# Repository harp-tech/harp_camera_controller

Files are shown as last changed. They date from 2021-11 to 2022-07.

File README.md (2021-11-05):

# Harp Camera Controlelr

This device contains the necessary circuitry to synchronously control and supply 2 cameras.

# Licensing

The code, designs, documentation, and photos available in this repository is free: you can redistribute it and/or modify it under the terms of the used license.
Each subdirectory will contain a license or, possibly, a set of licenses if it involves both hardware and software. Check files named LICENSE.

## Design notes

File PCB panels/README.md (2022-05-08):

# Harp Camera Controller Panels

## Licensing

The designs, documentation, and photos available in this repository are free: you can redistribute it and/or modify it under the terms of the used license.
Check file named LICENSE.

Copyright Filipe Carvalho 2021-2022

<br />This work is licensed under a <a rel="license" href="http://creativecommons.org/licenses/by-nc-sa/3.0/igo/">Creative Commons Attribution-NonCommercial-ShareAlike 3.0 IGO License</a>.

If your are interested in obtaining a license to sell this device, please contact info@oeps.tech

[1]: https://docs.google.com/spreadsheets/d/1aobmmEzBDethzIlrm1eg0eYkBqlyX3s9WbA9KgRwVQI/edit?usp=sharing

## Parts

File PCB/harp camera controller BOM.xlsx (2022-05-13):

Qty | Value | Package | Parts | MPN | Type
PCB COMPONENTS
2 | SN74LVC1G125DBVT | SOT23-5 | IC7, IC8 | SN74LVC1G125DBVT | SMD | -
1 | 74HCT125SO14 | SO14 | U5 | 74HCT125D,653 | SMD | -
3 | 74LVC126ASO14 | SO14 | U2, U3, U4 | 74LVC126AD,118 | SMD | -
2 | 74LVC1G240DBV | SOT23-5 | IC2, IC3 | SN74LVC1G240DBVR | SMD | -
1 | ATXMEGA32A4U-AU | QFP80P1200X1200X120-44N | IC6 | ATXMEGA32A4U-AUR | SMD | -
4 | BC850 | SOT23 | T1, T2, T3, T4 | BC850C,215 | SMD | -
1 | 330 Ohms @ 100MHz | R0603 | F1 | BLM18SG331TN1D | SMD | -
3 | BNC plug | 0731000105 | X3, X4, X5 | 73100-0105 | TH | -
23 | 100nF | C0402 | C2, C4, C5, C6, C8, C9, C14, C15, C16, C18, C19, C20, C24, C25, C26, C27, C28, C29, C31, C33, C34, C36, C38 | C1005X7R1H104K050BB | SMD | -
3 | 330pF | C0402 | C22, C30, C37 | C0402C331J5GACTU | SMD | -
1 | 4.7nF | C0402 | C1 | 885012205084 | SMD | -
2 | 47pF | C0402 | C10, C13 | 04025A470JAT2A | SMD | -
1 | 180nF | C0603 | C11 | GCG188R91H184KA01D | SMD
5 | 4.7uF | C0603 | C12, C21, C23, C32, C35 | C1608X6S1C475K080AC | SMD | -
1 | 4.7uF | C0805 | C3 | CL21A475KLCLQNC | SMD
1 | 100uF 16V | CT7343 | C17 | T491D107K016AT7280 | SMD
1 | 100u 25V | TT2D6 | C7 | EEU-FM1E101B | SMD | -
1 | DC_JACK2.1MM | DC_POWER_INPUT_2.1MM | PWR1 | 163-179PH-EX | TH | -
1 | FT232RL | SSOP28 | IC4 | FT232RL-REEL | SMD | -
1 | 10uH 3A | L_IHLP_PADS | L1 | IHLP2525CZER100M01 | SMD
2 | RED_LEDs | 569-011X-X00_LED_ARRAY | LED1, LED2 | 5690-111-100F | TH | -
1 | LT1765 | TSSOP16EXP | U1 | LT1765EFE#PBF | SMD | -
1 | PROG HEADER | MA03-2 | SV1 | 61300621121 | TH | -
1 | OSCILLATOR | OSCILLATOR_3.2X2.5 | OSC1 | O 32,0-JT32C-A-K-3,3-LF | SMD | ALTERNATIVE: DSC1001CI5-032.0000
1 | 10R | R0402 | R35 | CRCW040210R0FKEDC | SMD | -
18 | 10k | R0402 | R2, R3, R4, R5, R6, R7, R8, R10, R11, R15, R17, R21, R22, R23, R32, R33, R34, R36 | CRCW040210K0FKED | SMD | -
1 | 10k 0.1% | R0402 | R13 | CPF0402B10KE1 | SMD | -
6 | 1k | R0402 | R14, R16, R24, R25, R28, R29 | CRCW04021K00FKEDC | SMD | -
1 | 34k 0.1% | R0402 | R12 | ERA2AEB3402X | SMD
4 | 330R | R0402 | R26, R27, R30, R31 | RC0402FR-07330RL | SMD | -
4 | 100R | R0603 | R1, R18, R19, R20 | ERJ-3EKF1000V | SMD | -
1 | 40R@100MHz | R0805 | R9 | MI0805K400R-10 | SMD | -
2 | RJ45 | RJ45-NO-SHIELD | X1, X2 | 215877-1 | TH | -
1 | SSB43L-E3 | SMB | D1 | SSB43L-E3/52T | SMD | -
1 | CMDSH-3 | SOD323-R | D2 | CMDSH-3 | SMD | -
1 | SI8610BC-B-IS | SO-08 | IC10 | SI8610EC-B-IS | SMD | ALTERNATIVE: ADUM110N0BRZ
2 | CLCK_JACK | 35RASMT2BHNTRX | CLOCK_IN, CLOCK_OUT | 35RASMT2BHNTRX | SMD | -
2 | TLV70033DDCR | TSOT23-5 | IC5, IC9 | TLV70033DDCR | SMD | SIMILAR & AVAILABLE = LP5951MFX-3.3/NOPB >> DIGIKEY_PN: 296-47807-2-ND MOUSER_PN: 926-LP5951MFX33NOPB
1 | mini USB | 240-0002-1 | USB1 | UX60-MB-5S8 | SMD | END OF LIFE COMPONENT BY SEPTEMBER 2021
1 | USBLC6-2SC6 | SOT23-6L | IC1 | USBLC6-2SC6 | SMD | EQUIVALENT: RCLAMP0504S.TCT
POST-PRODUCTION
1 |  |  | Front Panel PCB | PCBWAY
1 |  |  | Rear Panel PCB | PCBWAY
1 |  |  | Enclosure | B5-080BK
4 |  |  | Bumper Cylindrical Dome 9.53mm | SJ-5306-CLEAR-3000/CASE
ACCESSORIES
1 |  |  | 3.5mm stereo jack cable 1.2 m, Black | AV13646
1 |  |  | 0.9 left angle USB cable | USB2HABM3RA
NOTES
 |  |  |  | Number of unique parts | 39
 |  |  |  | Number of unique SMD parts | 34
 |  |  |  | Number of unique TH parts | 5
 |  |  |  | Number of SMD parts | 101
 |  |  |  | Number of TH parts | 9
 |  | Optional
 |  | Holder: MF80BK2

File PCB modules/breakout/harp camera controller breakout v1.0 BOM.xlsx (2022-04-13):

Qty | Value | Package | Parts | MPN | Type | Distributor | Distributor PN
ASSEMBLY HOUSE
1 | Ultra-Low-Noise LDO 3.3V 250mA | SOT-23-5 | X1 | 215877-1 | TH | Farnell | 3363144
1 | Terminal block 7 ways 2.54 mm |  | X2 | 282834-7 | TH | Farnell | 3792975
POST-PRODUCTION
1 | Small Ethernet cable
NOTES
 |  |  |  | Number of unique parts | 2
 |  |  |  | Number of SMD parts | 0
 |  |  |  | Number of TH parts | 2

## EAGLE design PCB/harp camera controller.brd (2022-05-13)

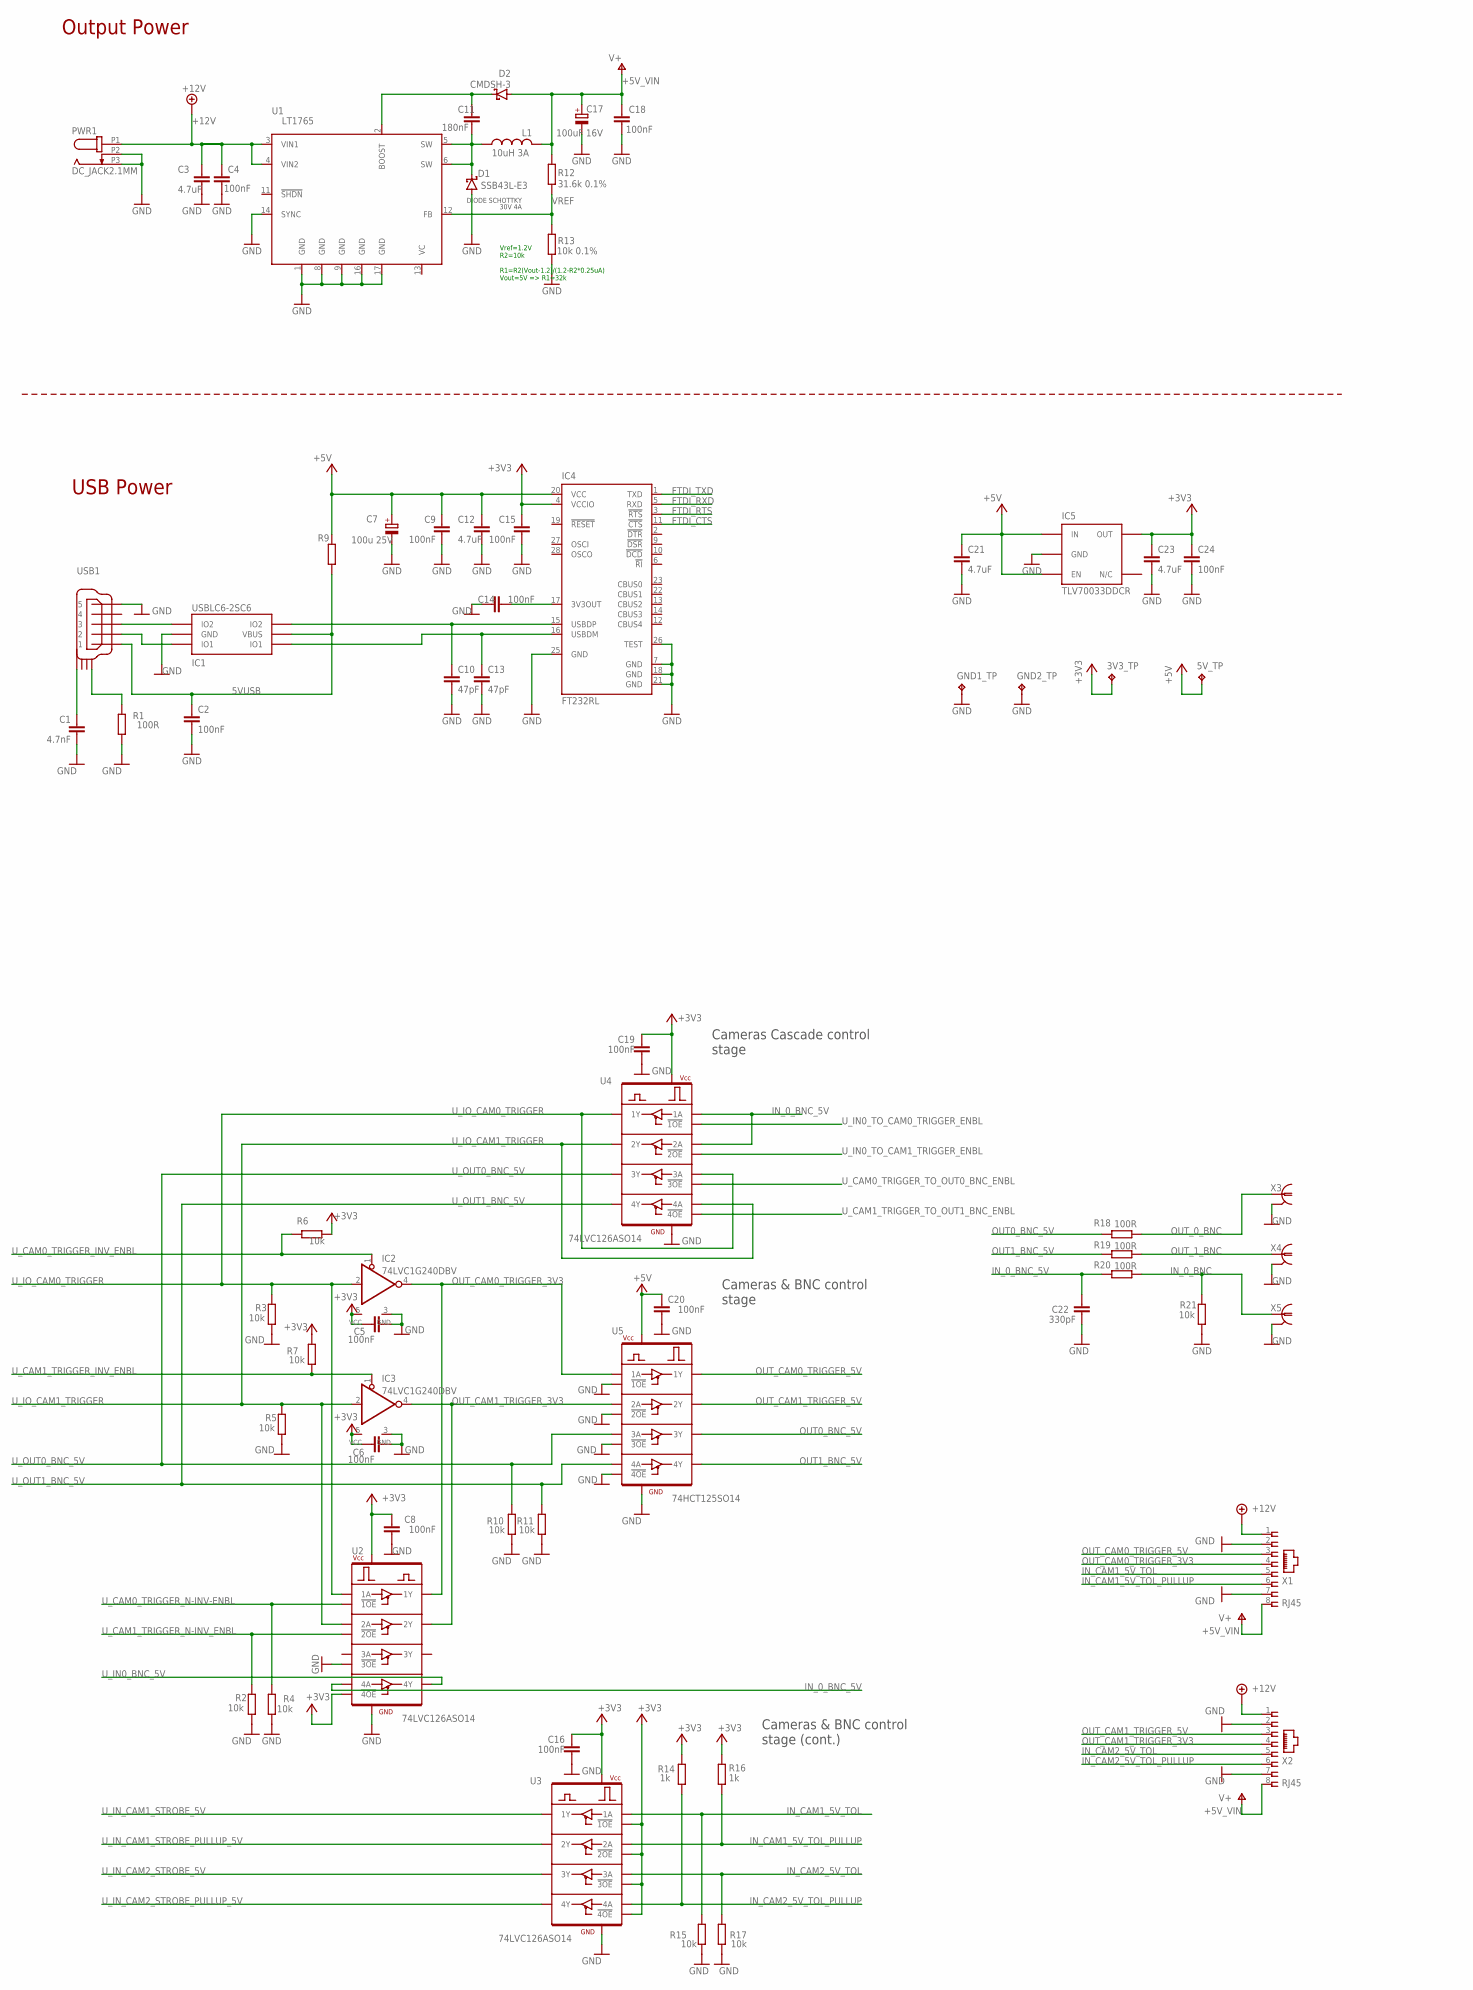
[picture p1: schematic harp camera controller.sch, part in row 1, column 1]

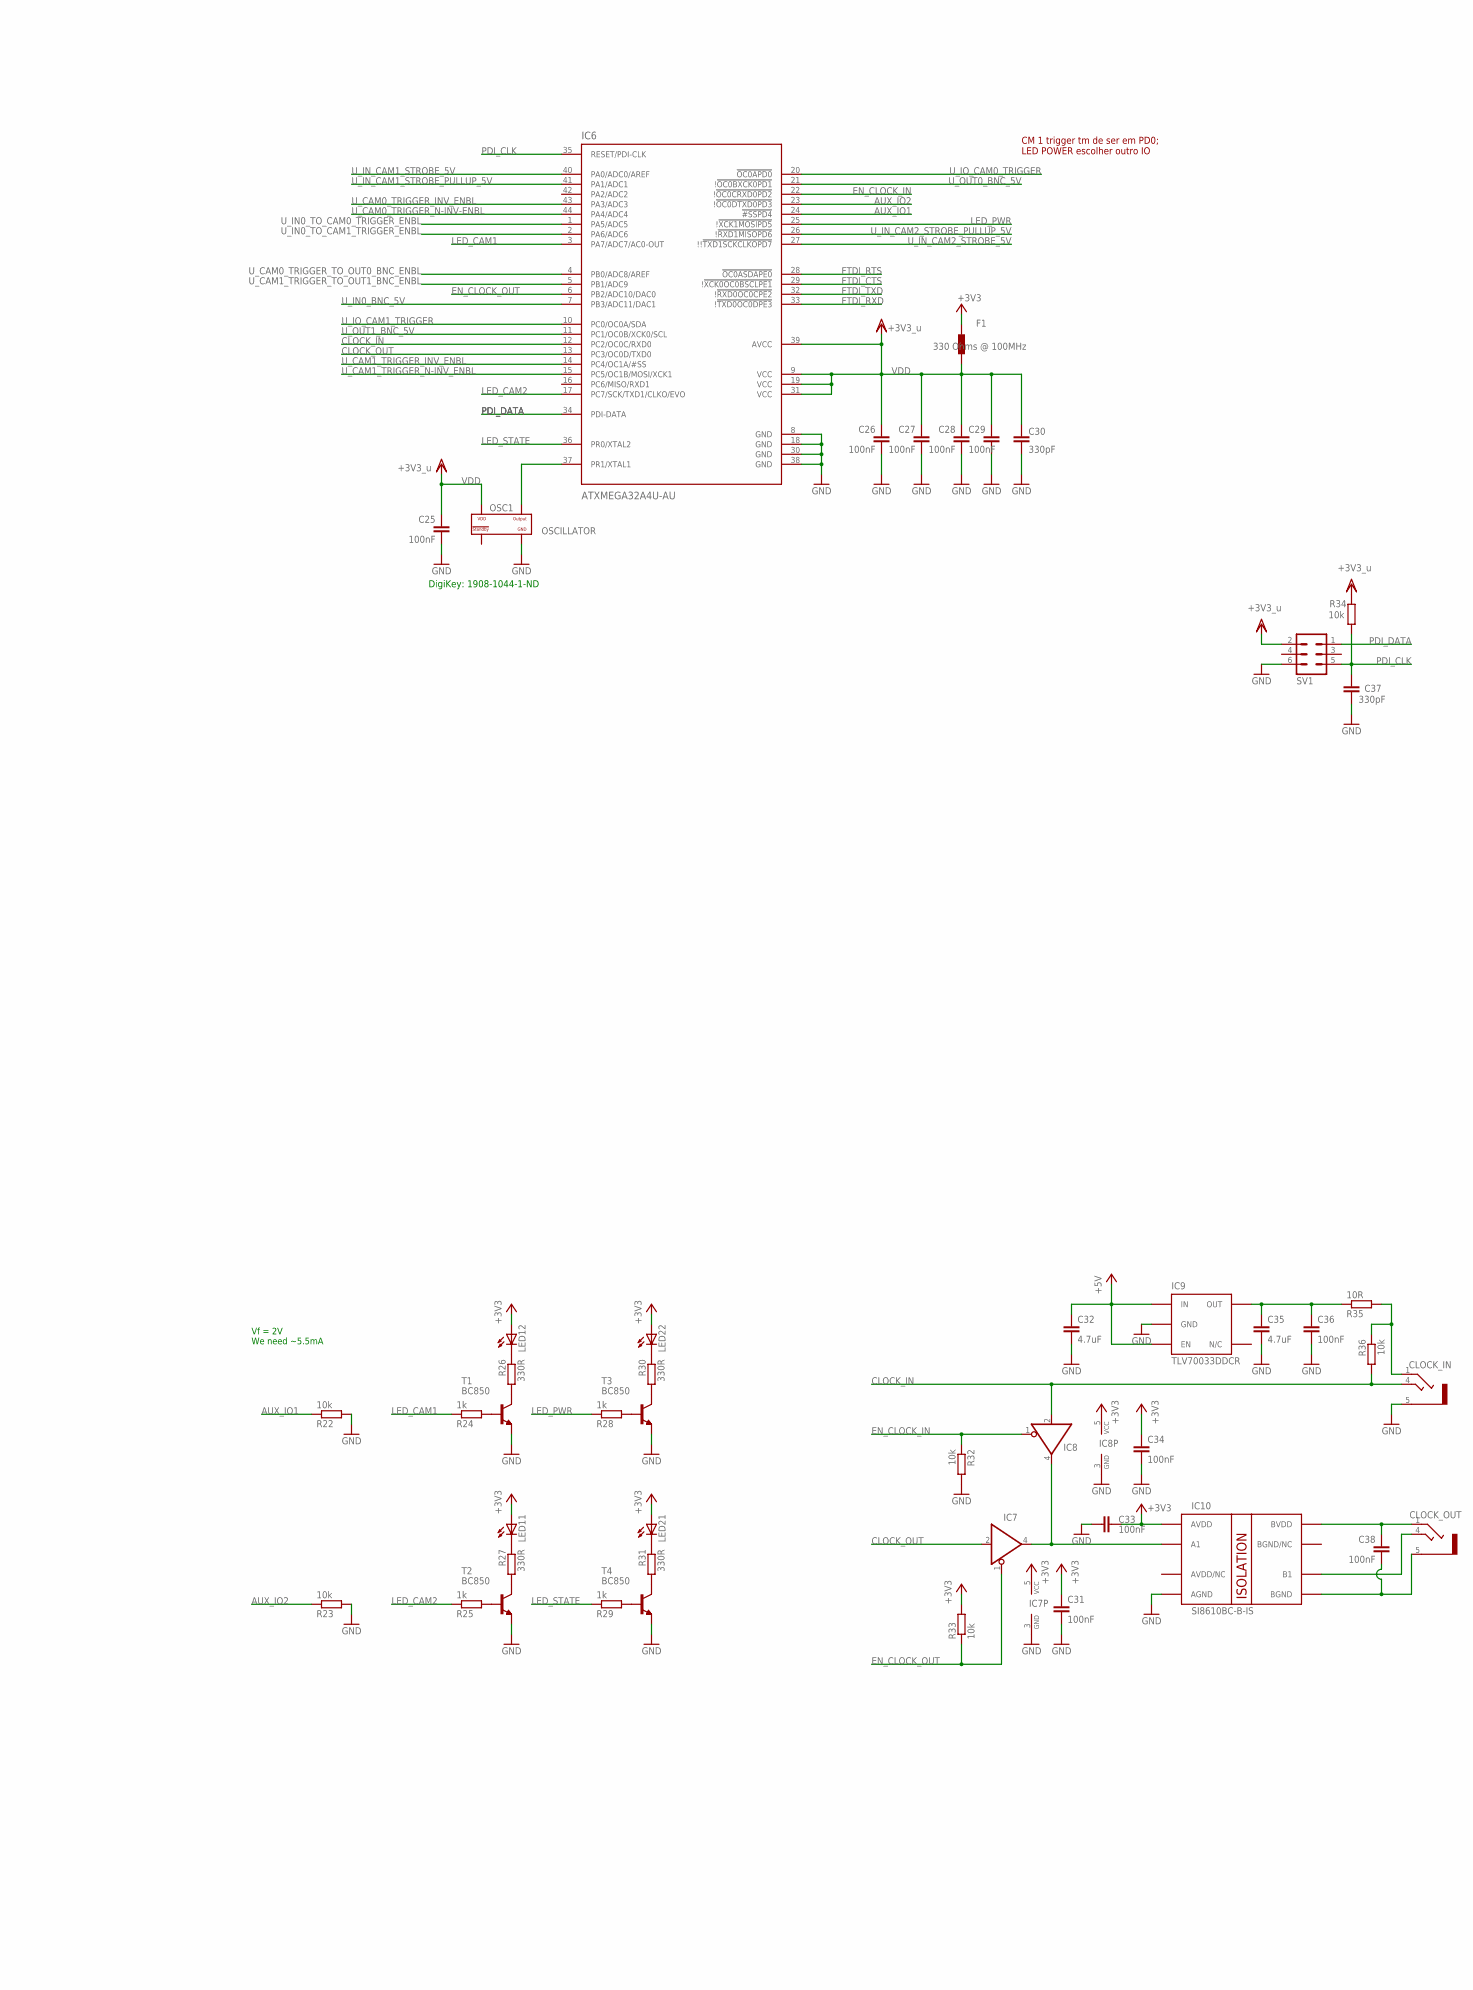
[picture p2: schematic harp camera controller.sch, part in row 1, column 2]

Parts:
3V3_TP, 5V_TP: TPPAD1-13; P1-13; MOUSER_PN N.A.; DIGIKEY_PN N.A.
C1: 4.7nF; C0402; MPN 885012205084; DIGIKEY_PN 732-12234-1-ND
C2, C4, C5, C6, C8, C9, C14, C15, C16, C18, C19, C20, C24, C25, C26, C27, C28, C29, C31, C33, C34, C36, C38: 100nF; C0402; MPN C1005X7R1H104K050BB; DIGIKEY_PN 445-5932-1-ND
C3: 4.7uF; C0805; MPN CL21A475KLCLQNC; DIGIKEY_PN 1276-6722-1-ND
C7: 100u 25V; TT2D6; MPN EEU-FM1E101B; DIGIKEY_PN P19702CT-ND
C10, C13: 47pF; C0402; MPN 04025A470JAT2A; DIGIKEY_PN 478-1078-1-ND
C11: 180nF; C0603; MPN GCG188R91H184KA01D; DIGIKEY_PN 490-GCG188R91H184KA01DCT-ND
C12, C21, C23, C32, C35: 4.7uF; C0603; MPN C1608X6S1C475K080AC; DIGIKEY_PN 445-9118-1-ND
C17: 100uF 16V; CT7343; MPN T491D107K016AT7280; DIGIKEY_PN 399-18066-1-ND
C22, C30, C37: 330pF; C0402; MPN C0402C331J5GACTU; DIGIKEY_PN 399-7787-1-ND
CLOCK_IN: CLCK_JACK; 35RASMT2BHNTRX; MOUSER_PN 502-35RASMT2BHNTRX; DIGIKEY_PN SC1489-1-ND
CLOCK_OUT: CLCK_JACK; 35RASMT2BHNTRX; MOUSER_PN 502-35RASMT2BHNTRX; DIGIKEY_PN SC1489-1-ND
D1: SSB43L-E3; SMB; MOUSER_PN 625-SSB43L-E3; DIGIKEY_PN SSB43L-E3/52TGICT-ND
D2: CMDSH-3; SOD323-R; MOUSER_PN 610-CMDSH-3; DIGIKEY_PN 1514-CMDSH-3TRPBFREECT-ND
F1: 330 Ohms @ 100MHz; R0603; MOUSER_PN 81-BLM18SG331TN1D; DIGIKEY_PN 490-3997-1-ND
GND1_TP, GND2_TP: TPPAD1-13; P1-13; MOUSER_PN N.A.; DIGIKEY_PN N.A.
IC1: USBLC6-2SC6; SOT23-6L; MOUSER_PN 511-USBLC6-2SC6; DIGIKEY_PN 497-5235-1-ND
IC2, IC3: 74LVC1G240DBV; SOT23-5; MOUSER_PN 595-SN74LVC1G240DBVR; DIGIKEY_PN 296-11609-1-ND
IC4: FT232RL; SSOP28; MOUSER_PN 895-FT232RL; DIGIKEY_PN 768-1007-1-ND
IC5, IC9: TLV70033DDCR; TSOT23-5; MOUSER_PN 595-TLV70033DDCR; DIGIKEY_PN 296-27937-1-ND
IC6: ATXMEGA32A4U-AU; QFP80P1200X1200X120-44N; MOUSER_PN 556-ATXMEGA32A4U-AU; DIGIKEY_PN ATXMEGA32A4U-AURCT-ND
IC7, IC8: SN74LVC1G125DBVT; SOT23-5; MOUSER_PN 595-SN74LVC1G125DBVT; DIGIKEY_PN 296-26595-1-ND
IC10: SI8610BC-B-IS; SO-08; MOUSER_PN 634-SI8610EC-B-IS; DIGIKEY_PN 336-2058-5-ND
L1: 10uH 3A; L_IHLP_PADS; MOUSER_PN 70-IHLP2525CZER100M0; DIGIKEY_PN 541-1013-2-ND
LED1, LED2: RED_LEDs; 569-011X-X00_LED_ARRAY; MOUSER_PN 645-569-0111-100F; DIGIKEY_PN 350-1782-ND
OSC1: OSCILLATOR; OSCILLATOR_3.2X2.5; MOUSER_PN N.A. - ALTERNATIVE ONLY; DIGIKEY_PN 1908-1044-1-ND
PWR1: DC_JACK2.1MM; DC_POWER_INPUT_2.1MM; MOUSER_PN 163-179PH; DIGIKEY_PN DIGIKEY N.A.
R1, R18, R19, R20: 100R; R0603; MPN ERJ-3EKF1000V; DIGIKEY_PN P100HCT-ND
R2, R3, R4, R5, R6, R7, R10, R11, R15, R17, R21, R22, R23, R32, R33, R34, R36: 10k; R0402; MPN CRCW040210K0FKED; DIGIKEY_PN 541-3959-1-ND
R9: 40R@100MHz; R0805; MPN MI0805K400R-10; DIGIKEY_PN 240-2389-1-ND
R12: 31.6k 0.1%; R0402; MPN RC0402FR-0740K2L; DIGIKEY_PN 311-40.2KLRCT-ND
R13: 10k 0.1%; R0402; MPN CRCW040210K0FKED; DIGIKEY_PN 541-3959-1-ND
R14, R16, R24, R25, R28, R29: 1k; R0402; MPN CRCW04021K00FKEDC; DIGIKEY_PN 541-3961-1-ND
R26, R27, R30, R31: 330R; R0402; MPN RC0402FR-07330RL; DIGIKEY_PN 311-330LRCT-ND
R35: 10R; R0402; MPN CRCW040210R0FKEDC; DIGIKEY_PN 541-3964-2-ND
SV1: PROG HEADER; MA03-2; MOUSER_PN 710-61300621121; DIGIKEY_PN 732-5295-ND
T1, T2, T3, T4: BC850; SOT23; MOUSER_PN 771-BC850C-T/R; DIGIKEY_PN 1727-4862-1-ND
U1: LT1765; TSSOP16EXP; MOUSER_PN 584-LT1765EFE#TRPBF; DIGIKEY_PN LT1765EFE#PBF-ND
U2, U3, U4: 74LVC126ASO14; SO14; MOUSER_PN 771-LVC126AD118; DIGIKEY_PN 1727-6365-1-ND
U5: 74HCT125SO14; SO14; MOUSER_PN 771-74HCT125D-T; DIGIKEY_PN 1727-2834-1-ND
USB1: mini USB; 240-0002-1; MOUSER_PN 798-UX60-MB-5S8; DIGIKEY_PN H2960TR-ND
X1, X2: RJ45; RJ45-NO-SHIELD; MOUSER_PN 571-2158771; DIGIKEY_PN A105009CT-ND
X3, X4, X5: BNC plug; 0731000105; MOUSER_PN N.A.; DIGIKEY_PN WM5524-ND

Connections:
5VUSB: C2.1, IC1.P$5 (VBUS), R9.2, USB1.P$1 (1)
+3V3: 3V3_TP.TP, C5.1, C6.1, C8.1, C15.1, C16.1, C19.1, C23.1, C24.1, C31.1, C33.1, C34.1, F1.2, IC2.5 (VCC), IC3.5 (VCC), IC4.4 (VCCIO), IC5.5 (OUT), IC7.5 (VCC), IC8.5 (VCC), IC10.1 (AVDD), LED1.A1 (A), LED1.A2 (A), LED2.A1 (A), LED2.A2 (A), R6.1, R7.1, R14.1, R16.1, R33.2, U2.13 (!4OE), U2.14 (VCC), U3.1 (!1OE), U3.4 (!2OE), U3.10 (!3OE), U3.13 (!4OE), U3.14 (VCC), U4.14 (VCC)
+5V: 5V_TP.TP, C7.+, C9.1, C12.1, C20.1, C21.1, C32.1, IC4.20 (VCC), IC5.1 (IN), IC5.3 (EN), IC9.1 (IN), IC9.3 (EN), R9.1, U5.14 (VCC)
+5V_VIN: C17.+, C18.1, D2.A, L1.1, R12.2, X1.8, X2.8
+12V: C3.1, C4.1, PWR1.P1 (1), U1.3 (VIN1), U1.4 (VIN2), X1.1, X2.1
AUX_IO1: IC6.24 (!#SSPD4), R22.1
AUX_IO2: IC6.23 (!!OC0DTXD0PD3), R23.1
CLOCK_IN: CLOCK_IN.4, IC6.12 (PC2/OC0C/RXD0), IC8.2 (I), R36.2
CLOCK_OUT: IC6.13 (PC3/OC0D/TXD0), IC7.2 (I)
EN_CLOCK_IN: IC6.22 (!!OC0CRXD0PD2), IC8.1 (OE), R32.1
EN_CLOCK_OUT: IC6.6 (PB2/ADC10/DAC0), IC7.1 (OE), R33.1
FTDI_CTS: IC4.11 (!CTS), IC6.29 (!!XCK0OC0BSCLPE1)
FTDI_RTS: IC4.3 (!RTS), IC6.28 (!OC0ASDAPE0)
FTDI_RXD: IC4.5 (RXD), IC6.33 (!!TXD0OC0DPE3)
FTDI_TXD: IC4.1 (TXD), IC6.32 (!!RXD0OC0CPE2)
GND: C1.2, C2.2, C3.2, C4.2, C5.2, C6.2, C7.-, C8.2, C9.2, C10.2, C12.2, C13.2, C14.2, C15.2, C16.2, C17.-, C18.2, C19.2, C20.2, C21.2, C22.2, C23.2, C24.2, C25.2, C26.2, C27.2, C28.2, C29.2, C30.2, C31.2, C32.2, C33.2, C34.2, C35.2, C36.2, C37.2, CLOCK_IN.5, D1.A, GND1_TP.TP, GND2_TP.TP, IC1.P$2 (GND), IC2.3 (GND), IC3.3 (GND), IC4.7 (GND), IC4.18 (GND), IC4.21 (GND), IC4.25 (GND), IC4.26 (TEST), IC5.2 (GND), IC6.8 (GND), IC6.18 (GND), IC6.30 (GND), IC6.38 (GND), IC7.3 (GND), IC8.3 (GND), IC9.2 (GND), IC10.4 (AGND), OSC1.P$2 (GND), PWR1.P2 (2), PWR1.P3 (3), R1.2, R2.1, R3.1, R4.1, R5.1, R10.2, R11.2, R13.1, R15.1, R17.1, R21.1, R22.2, R23.2, R32.2, SV1.6, T1.2 (E), T2.2 (E), T3.2 (E), T4.2 (E), U1.1 (GND), U1.8 (GND), U1.9 (GND), U1.14 (SYNC), U1.16 (GND), U1.17 (GND), U2.7 (GND), U2.10 (!3OE), U3.7 (GND), U4.7 (GND), U5.1 (!1OE), U5.4 (!2OE), U5.7 (GND), U5.10 (!3OE), U5.13 (!4OE), USB1.P$5 (5), X1.2, X1.7, X2.2, X2.7, X3.2, X3.3 (2), X4.2, X4.3 (2), X5.2, X5.3 (2)
GND_ISO: C38.2, CLOCK_OUT.5, IC10.5 (BGND)
IN_0_BNC: R20.1, R21.2, X5.1
IN_0_BNC_5V: C22.1, R20.2, U2.12 (4A), U4.2 (1A), U4.5 (2A)
IN_CAM1_5V_TOL: R15.2, U3.2 (1A), X1.5
IN_CAM1_5V_TOL_PULLUP: R16.2, U3.5 (2A), X1.6
IN_CAM2_5V_TOL: R17.2, U3.9 (3A), X2.5
IN_CAM2_5V_TOL_PULLUP: R14.2, U3.12 (4A), X2.6
LED_CAM1: IC6.3 (PA7/ADC7/AC0-OUT), R24.1
LED_CAM2: IC6.17 (PC7/SCK/TXD1/CLKO/EVO), R25.1
LED_PWR: IC6.25 (!!XCK1MOSIPD5), R28.1
LED_STATE: IC6.36 (PR0/XTAL2), R29.1
unnamed: R24.2, T1.1 (B)
unnamed: CLOCK_OUT.4, IC10.6 (B1)
unnamed: C38.1, CLOCK_OUT.1, IC10.8 (BVDD)
unnamed: R26.2, T1.3 (C)
unnamed: C11.2, D1.C, L1.2, U1.5 (SW), U1.6 (SW)
unnamed: C11.1, D2.C, U1.2 (BOOST)
unnamed: R25.2, T2.1 (B)
unnamed: C14.1, IC4.17 (3V3OUT)
unnamed: IC1.P$1 (IO1), USB1.P$2 (2)
unnamed: CLOCK_IN.1, R35.2, R36.1
unnamed: C35.1, C36.1, IC9.5 (OUT), R35.1
unnamed: IC7.4 (O), IC8.4 (O), IC10.2 (A1)
unnamed: R27.2, T2.3 (C)
unnamed: IC1.P$3 (IO2), USB1.P$3 (3)
unnamed: R28.2, T3.1 (B)
unnamed: R30.2, T3.3 (C)
unnamed: R29.2, T4.1 (B)
unnamed: C1.1, USB1.SHIELD_4
unnamed: R31.2, T4.3 (C)
unnamed: R1.1, USB1.SHIELD_1
unnamed: LED2.C1 (C), R31.1
unnamed: LED2.C2 (C), R30.1
unnamed: LED1.C2 (C), R26.1
unnamed: LED1.C1 (C), R27.1
OSC2: IC6.37 (PR1/XTAL1), OSC1.P$3 (OUTPUT)
OUT0_BNC_5V: R18.2, U5.8 (3Y)
OUT1_BNC_5V: R19.2, U5.11 (4Y)
OUT_0_BNC: R18.1, X3.1
OUT_1_BNC: R19.1, X4.1
OUT_CAM0_TRIGGER_3V3: IC2.4 (O), U2.3 (1Y), U5.2 (1A), X1.4
OUT_CAM0_TRIGGER_5V: U5.3 (1Y), X1.3
OUT_CAM1_TRIGGER_3V3: IC3.4 (O), U2.6 (2Y), U5.5 (2A), X2.4
OUT_CAM1_TRIGGER_5V: U5.6 (2Y), X2.3
PDI_CLK: C37.1, IC6.35 (RESET/PDI-CLK), R34.1, SV1.5
PDI_DATA: IC6.34 (PDI-DATA), SV1.1
USBDM: C13.1, IC1.P$6 (IO1), IC4.16 (USBDM)
USBDP: C10.1, IC1.P$4 (IO2), IC4.15 (USBDP)
U_CAM0_TRIGGER_INV_ENBL: IC2.1 (OE), IC6.43 (PA3/ADC3), R6.2
U_CAM0_TRIGGER_N-INV-ENBL: IC6.44 (PA4/ADC4), R4.2, U2.1 (!1OE)
U_CAM0_TRIGGER_TO_OUT0_BNC_ENBL: IC6.4 (PB0/ADC8/AREF), U4.10 (!3OE)
U_CAM1_TRIGGER_INV_ENBL: IC3.1 (OE), IC6.14 (PC4/OC1A/#SS), R7.2
U_CAM1_TRIGGER_N-INV_ENBL: IC6.15 (PC5/OC1B/MOSI/XCK1), R2.2, U2.4 (!2OE)
U_CAM1_TRIGGER_TO_OUT1_BNC_ENBL: IC6.5 (PB1/ADC9), U4.13 (!4OE)
U_IN0_BNC_5V: IC6.7 (PB3/ADC11/DAC1), U2.11 (4Y)
U_IN0_TO_CAM0_TRIGGER_ENBL: IC6.1 (PA5/ADC5), U4.1 (!1OE)
U_IN0_TO_CAM1_TRIGGER_ENBL: IC6.2 (PA6/ADC6), U4.4 (!2OE)
U_IN_CAM1_STROBE_5V: IC6.40 (PA0/ADC0/AREF), U3.3 (1Y)
U_IN_CAM1_STROBE_PULLUP_5V: IC6.41 (PA1/ADC1), U3.6 (2Y)
U_IN_CAM2_STROBE_5V: IC6.27 (!!!TXD1SCKCLKOPD7), U3.8 (3Y)
U_IN_CAM2_STROBE_PULLUP_5V: IC6.26 (!!RXD1MISOPD6), U3.11 (4Y)
U_IO_CAM0_TRIGGER: IC2.2 (I), IC6.20 (!OC0APD0), R3.2, U2.2 (1A), U4.3 (1Y), U4.9 (3A)
U_IO_CAM1_TRIGGER: IC3.2 (I), IC6.10 (PC0/OC0A/SDA), R5.2, U2.5 (2A), U4.6 (2Y), U4.12 (4A)
U_OUT0_BNC_5V: IC6.21 (!!OC0BXCK0PD1), R10.1, U4.8 (3Y), U5.9 (3A)
U_OUT1_BNC_5V: IC6.11 (PC1/OC0B/XCK0/SCL), R11.1, U4.11 (4Y), U5.12 (4A)
VDD: C25.1, C26.1, C27.1, C28.1, C29.1, C30.1, F1.1, IC6.9 (VCC), IC6.19 (VCC), IC6.31 (VCC), IC6.39 (AVCC), OSC1.P$4 (VDD), R34.2, SV1.2
VREF: R12.1, R13.2, U1.12 (FB)

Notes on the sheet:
Vf = 2V We need ~5.5mA
DigiKey: 1908-1044-1-ND
Vref=1.2V R2=10k R1=R2(Vout-1.2)/(1.2-R2*0.25uA) Vout=5V => R1=32k
DIODE SCHOTTKY 30V 4A
Output Power
USB Power
CM 1 trigger tm de ser em PD0; LED POWER escolher outro IO
Cameras & BNC control stage (cont.)
Cameras Cascade control stage
Cameras & BNC control stage

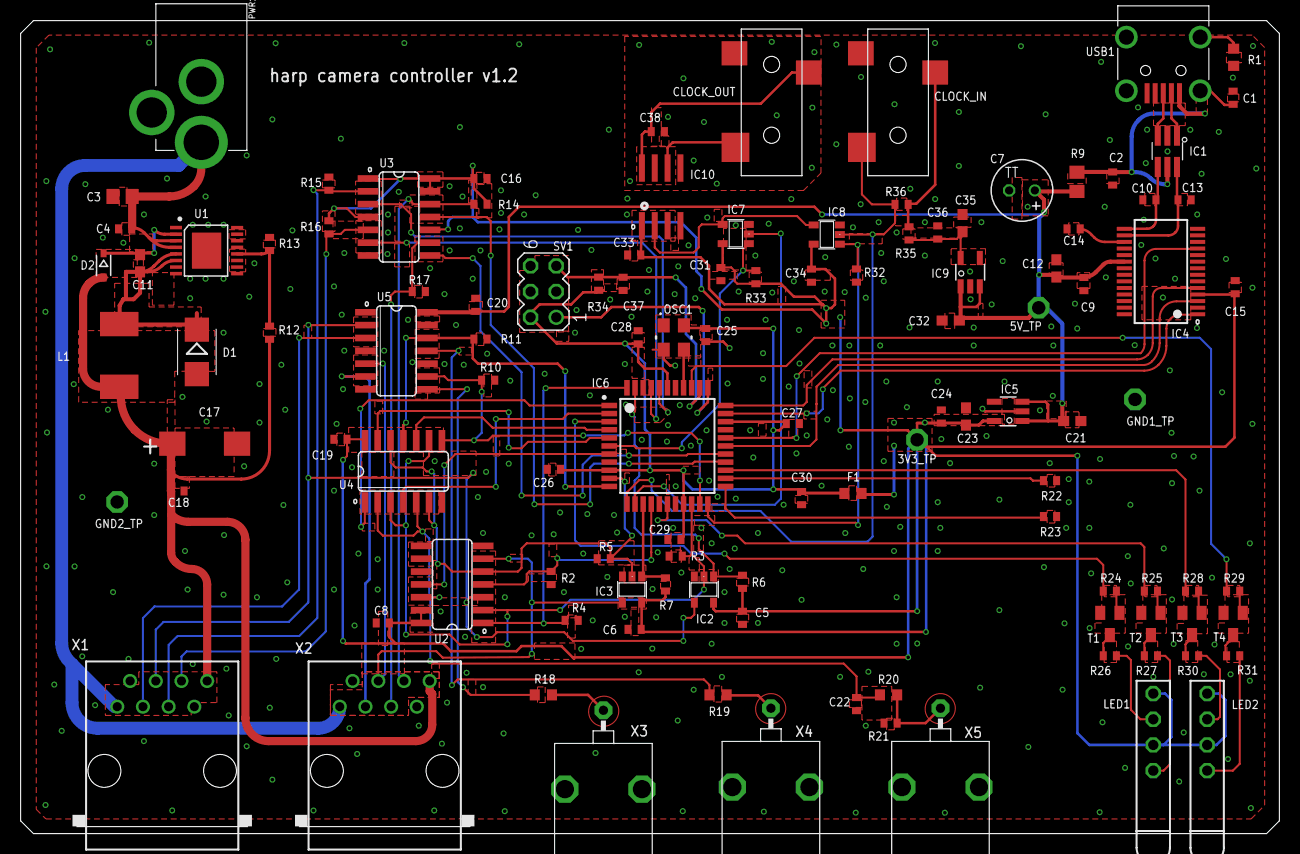
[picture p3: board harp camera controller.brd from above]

Board: 2 copper layers, 124.5 x 80.4 mm, 113 parts (0 on the bottom side), 83 nets.

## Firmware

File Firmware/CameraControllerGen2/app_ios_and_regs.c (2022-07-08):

#include <avr/io.h>
#include "hwbp_core_types.h"
#include "app_ios_and_regs.h"

/************************************************************************/
/* Configure and initialize IOs                                         */
/************************************************************************/
void init_ios(void)
{	/* Configure input pins */
	io_pin2in(&PORTA, 0, PULL_IO_TRISTATE, SENSE_IO_EDGES_BOTH);         // CAM0_STROBE
	io_pin2in(&PORTA, 1, PULL_IO_TRISTATE, SENSE_IO_EDGES_BOTH);         // CAM0_STROBE_PU
	io_pin2in(&PORTD, 7, PULL_IO_TRISTATE, SENSE_IO_EDGES_BOTH);         // CAM1_STROBE
	io_pin2in(&PORTD, 6, PULL_IO_TRISTATE, SENSE_IO_EDGES_BOTH);         // CAM1_STROBE_PU
	io_pin2in(&PORTB, 3, PULL_IO_TRISTATE, SENSE_IO_EDGES_BOTH);         // INPUT0
	io_pin2in(&PORTD, 0, PULL_IO_TRISTATE, SENSE_IO_EDGE_RISING);        // CAM0
	io_pin2in(&PORTD, 1, PULL_IO_TRISTATE, SENSE_IO_NO_INT_USED);        // OUT0
	io_pin2in(&PORTC, 0, PULL_IO_TRISTATE, SENSE_IO_EDGE_RISING);        // CAM1
	io_pin2in(&PORTC, 1, PULL_IO_TRISTATE, SENSE_IO_NO_INT_USED);        // OUT1

	/* Configure input interrupts */
	io_set_int(&PORTA, INT_LEVEL_LOW, 0, (1<<0), false);                 // CAM0_STROBE
	io_set_int(&PORTA, INT_LEVEL_LOW, 0, (1<<1), false);                 // CAM0_STROBE_PU
	io_set_int(&PORTD, INT_LEVEL_LOW, 0, (1<<7), false);                 // CAM1_STROBE
	io_set_int(&PORTD, INT_LEVEL_LOW, 0, (1<<6), false);                 // CAM1_STROBE_PU
	io_set_int(&PORTB, INT_LEVEL_LOW, 1, (1<<3), false);                 // INPUT0
	io_set_int(&PORTD, INT_LEVEL_LOW, 1, (1<<0), false);                 // CAM0
	io_set_int(&PORTC, INT_LEVEL_LOW, 1, (1<<0), false);                 // CAM1

	/* Configure output pins */
	io_pin2out(&PORTA, 7, OUT_IO_DIGITAL, IN_EN_IO_EN);                  // LED_CAM0
	io_pin2out(&PORTC, 7, OUT_IO_DIGITAL, IN_EN_IO_EN);                  // LED_CAM1
	io_pin2out(&PORTR, 0, OUT_IO_DIGITAL, IN_EN_IO_EN);                  // LED_STATE
	io_pin2out(&PORTD, 5, OUT_IO_DIGITAL, IN_EN_IO_EN);                  // LED_PWR
	io_pin2out(&PORTA, 3, OUT_IO_DIGITAL, IN_EN_IO_EN);                  // EN_CAM0_TRIGGER_INV
	io_pin2out(&PORTA, 4, OUT_IO_DIGITAL, IN_EN_IO_EN);                  // EN_CAM0_TRIGGER_N_INV
	io_pin2out(&PORTC, 4, OUT_IO_DIGITAL, IN_EN_IO_EN);                  // EN_CAM1_TRIGGER_INV
	io_pin2out(&PORTC, 5, OUT_IO_DIGITAL, IN_EN_IO_EN);                  // EN_CAM1_TRIGGER_N_INV
	io_pin2out(&PORTB, 0, OUT_IO_DIGITAL, IN_EN_IO_EN);                  // EN_CAM0_TO_OUT0
	io_pin2out(&PORTB, 1, OUT_IO_DIGITAL, IN_EN_IO_EN);                  // EN_CAM1_TO_OUT1
	io_pin2out(&PORTA, 5, OUT_IO_DIGITAL, IN_EN_IO_EN);                  // EN_IN0_TO_CAM0
	io_pin2out(&PORTA, 6, OUT_IO_DIGITAL, IN_EN_IO_EN);                  // EN_IN0_TO_CAM1
	io_pin2out(&PORTD, 2, OUT_IO_DIGITAL, IN_EN_IO_EN);                  // EN_CLOCK_IN
	io_pin2out(&PORTB, 2, OUT_IO_DIGITAL, IN_EN_IO_EN);                  // EN_CLOCK_OUT

	/* Initialize output pins */
	clr_LED_CAM0;
	clr_LED_CAM1;
	clr_LED_STATE;
	clr_LED_PWR;
	clr_EN_CAM0_TRIGGER_INV;
	clr_EN_CAM0_TRIGGER_N_INV;
	clr_EN_CAM1_TRIGGER_INV;
	clr_EN_CAM1_TRIGGER_N_INV;
	clr_EN_CAM0_TO_OUT0;
	clr_EN_CAM1_TO_OUT1;
	clr_EN_IN0_TO_CAM0;
	clr_EN_IN0_TO_CAM1;
	set_EN_CLOCK_IN;
	clr_EN_CLOCK_OUT;
}

/************************************************************************/
/* Registers' stuff                                                     */
/************************************************************************/
AppRegs app_regs;

uint8_t app_regs_type[] = {
	TYPE_U8,
	TYPE_U8,
	TYPE_U8,
	TYPE_U8,
	TYPE_U8,
	TYPE_U8,
	TYPE_U32,
	TYPE_U32,
	TYPE_U8,
	TYPE_U8,
	TYPE_U8,
	TYPE_U8,
	TYPE_U8,
	TYPE_U16,
	TYPE_U16,
	TYPE_U8,
	TYPE_U8,
	TYPE_U8,
	TYPE_U8,
	TYPE_U8,
	TYPE_U16,
	TYPE_U16,
	TYPE_U8,
	TYPE_U8,
	TYPE_U8,
	TYPE_U8,
	TYPE_U8,
	TYPE_U8,
	TYPE_U8,
	TYPE_U8,
	TYPE_U8,
	TYPE_U8,
	TYPE_U8
};

uint16_t app_regs_n_elements[] = {
	1,
	1,
	1,
	1,
	1,
	1,
	1,
	1,
	1,
	1,
	1,
	1,
	1,
	1,
	1,
	1,
	1,
	1,
	1,
	1,
	1,
	1,
	1,
	1,
	1,
	1,
	1,
	1,
	1,
	1,
	1,
	1,
	1
};

uint8_t *app_regs_pointer[] = {
	(uint8_t*)(&app_regs.REG_CAM0_EVENT),
	(uint8_t*)(&app_regs.REG_CAM1_EVENT),
	(uint8_t*)(&app_regs.REG_CAM0_EVENT_CONFIG),
	(uint8_t*)(&app_regs.REG_CAM1_EVENT_CONFIG),
	(uint8_t*)(&app_regs.REG_START_AND_STOP),
	(uint8_t*)(&app_regs.REG_START_AND_STOP_TIMESTAMPED),
	(uint8_t*)(&app_regs.REG_START_TIMESTAMP),
	(uint8_t*)(&app_regs.REG_STOP_TIMESTAMP),
	(uint8_t*)(&app_regs.REG_RESERVED0),
	(uint8_t*)(&app_regs.REG_RESERVED1),
	(uint8_t*)(&app_regs.REG_CAM0_TRIGGER_CONFIG),
	(uint8_t*)(&app_regs.REG_CAM0_TRIGGER_INVERTED),
	(uint8_t*)(&app_regs.REG_CAM0_STROBE_SOURCE),
	(uint8_t*)(&app_regs.REG_CAM0_TRIGGER_FREQUENCY),
	(uint8_t*)(&app_regs.REG_CAM0_TRIGGER_DURATION_US),
	(uint8_t*)(&app_regs.REG_RESERVED2),
	(uint8_t*)(&app_regs.REG_RESERVED3),
	(uint8_t*)(&app_regs.REG_CAM1_TRIGGER_CONFIG),
	(uint8_t*)(&app_regs.REG_CAM1_TRIGGER_INVERTED),
	(uint8_t*)(&app_regs.REG_CAM1_STROBE_SOURCE),
	(uint8_t*)(&app_regs.REG_CAM1_TRIGGER_FREQUENCY),
	(uint8_t*)(&app_regs.REG_CAM1_TRIGGER_DURATION_US),
	(uint8_t*)(&app_regs.REG_RESERVED4),
	(uint8_t*)(&app_regs.REG_RESERVED5),
	(uint8_t*)(&app_regs.REG_OUT0_CONFIG),
	(uint8_t*)(&app_regs.REG_OUT1_CONFIG),
	(uint8_t*)(&app_regs.REG_RESERVED6),
	(uint8_t*)(&app_regs.REG_RESERVED7),
	(uint8_t*)(&app_regs.REG_OUT_SET),
	(uint8_t*)(&app_regs.REG_OUT_CLEAR),
	(uint8_t*)(&app_regs.REG_OUT_TOGGLE),
	(uint8_t*)(&app_regs.REG_OUT_WRITE),
	(uint8_t*)(&app_regs.REG_IN_STATE)
};

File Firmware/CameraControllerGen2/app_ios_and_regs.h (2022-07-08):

#ifndef _APP_IOS_AND_REGS_H_
#define _APP_IOS_AND_REGS_H_
#include "cpu.h"

void init_ios(void);
/************************************************************************/
/* Definition of input pins                                             */
/************************************************************************/
// CAM0_STROBE            Description: Strobe from camera 0
// CAM0_STROBE_PU         Description: Pull-up strobe from camera 0
// CAM1_STROBE            Description: Strobe from camera 1
// CAM1_STROBE_PU         Description: Pull-up strobe from camera 1
// INPUT0                 Description: Digital input 0
// CAM0                   Description: Trigger for camera 0
// OUT0                   Description: Digital output 0
// CAM1                   Description: Trigger for camera 1
// OUT1                   Description: Digital output 1

#define read_CAM0_STROBE read_io(PORTA, 0)      // CAM0_STROBE
#define read_CAM0_STROBE_PU read_io(PORTA, 1)   // CAM0_STROBE_PU
#define read_CAM1_STROBE read_io(PORTD, 7)      // CAM1_STROBE
#define read_CAM1_STROBE_PU read_io(PORTD, 6)   // CAM1_STROBE_PU
#define read_INPUT0 read_io(PORTB, 3)           // INPUT0
#define read_CAM0 read_io(PORTD, 0)             // CAM0
#define read_OUT0 read_io(PORTD, 1)             // OUT0
#define read_CAM1 read_io(PORTC, 0)             // CAM1
#define read_OUT1 read_io(PORTC, 1)             // OUT1

/************************************************************************/
/* Definition of output pins                                            */
/************************************************************************/
// LED_CAM0               Description: Camera's 0 LED
// LED_CAM1               Description: Camera's 1 LED
// LED_STATE              Description: Power's LED
// LED_PWR                Description: Power's LED
// EN_CAM0_TRIGGER_INV    Description: Enable camera's 0 direct trigger
// EN_CAM0_TRIGGER_N_INV  Description: Enable camera's 0 inverted trigger
// EN_CAM1_TRIGGER_INV    Description: Enable camera's 1 direct trigger
// EN_CAM1_TRIGGER_N_INV  Description: Enable camera's 1 inverted trigger
// EN_CAM0_TO_OUT0        Description: Connect CAM0 signal to OUT0
// EN_CAM1_TO_OUT1        Description: Connect CAM1 signal to OUT1
// EN_IN0_TO_CAM0         Description: Connect IN0 signal to CAM0
// EN_IN0_TO_CAM1         Description: Connect IN0 signal to CAM1
// EN_CLOCK_IN            Description: Digital output 1
// EN_CLOCK_OUT           Description: Digital output 1

/* LED_CAM0 */
#define set_LED_CAM0 set_io(PORTA, 7)
#define clr_LED_CAM0 clear_io(PORTA, 7)
#define tgl_LED_CAM0 toggle_io(PORTA, 7)
#define read_LED_CAM0 read_io(PORTA, 7)

/* LED_CAM1 */
#define set_LED_CAM1 set_io(PORTC, 7)
#define clr_LED_CAM1 clear_io(PORTC, 7)
#define tgl_LED_CAM1 toggle_io(PORTC, 7)
#define read_LED_CAM1 read_io(PORTC, 7)

/* LED_STATE */
#define set_LED_STATE set_io(PORTR, 0)
#define clr_LED_STATE clear_io(PORTR, 0)
#define tgl_LED_STATE toggle_io(PORTR, 0)
#define read_LED_STATE read_io(PORTR, 0)

/* LED_PWR */
#define set_LED_PWR set_io(PORTD, 5)
#define clr_LED_PWR clear_io(PORTD, 5)
#define tgl_LED_PWR toggle_io(PORTD, 5)
#define read_LED_PWR read_io(PORTD, 5)

/* EN_CAM0_TRIGGER_INV */
#define set_EN_CAM0_TRIGGER_INV clear_io(PORTA, 3)
#define clr_EN_CAM0_TRIGGER_INV set_io(PORTA, 3)
#define tgl_EN_CAM0_TRIGGER_INV toggle_io(PORTA, 3)
#define read_EN_CAM0_TRIGGER_INV read_io(PORTA, 3)

/* EN_CAM0_TRIGGER_N_INV */
#define set_EN_CAM0_TRIGGER_N_INV set_io(PORTA, 4)
#define clr_EN_CAM0_TRIGGER_N_INV clear_io(PORTA, 4)
#define tgl_EN_CAM0_TRIGGER_N_INV toggle_io(PORTA, 4)
#define read_EN_CAM0_TRIGGER_N_INV read_io(PORTA, 4)

/* EN_CAM1_TRIGGER_INV */
#define set_EN_CAM1_TRIGGER_INV clear_io(PORTC, 4)
#define clr_EN_CAM1_TRIGGER_INV set_io(PORTC, 4)
#define tgl_EN_CAM1_TRIGGER_INV toggle_io(PORTC, 4)
#define read_EN_CAM1_TRIGGER_INV read_io(PORTC, 4)

/* EN_CAM1_TRIGGER_N_INV */
#define set_EN_CAM1_TRIGGER_N_INV set_io(PORTC, 5)
#define clr_EN_CAM1_TRIGGER_N_INV clear_io(PORTC, 5)
#define tgl_EN_CAM1_TRIGGER_N_INV toggle_io(PORTC, 5)
#define read_EN_CAM1_TRIGGER_N_INV read_io(PORTC, 5)

/* EN_CAM0_TO_OUT0 */
#define set_EN_CAM0_TO_OUT0 set_io(PORTB, 0)
#define clr_EN_CAM0_TO_OUT0 clear_io(PORTB, 0)
#define tgl_EN_CAM0_TO_OUT0 toggle_io(PORTB, 0)
#define read_EN_CAM0_TO_OUT0 read_io(PORTB, 0)

/* EN_CAM1_TO_OUT1 */
#define set_EN_CAM1_TO_OUT1 set_io(PORTB, 1)
#define clr_EN_CAM1_TO_OUT1 clear_io(PORTB, 1)
#define tgl_EN_CAM1_TO_OUT1 toggle_io(PORTB, 1)
#define read_EN_CAM1_TO_OUT1 read_io(PORTB, 1)

/* EN_IN0_TO_CAM0 */
#define set_EN_IN0_TO_CAM0 set_io(PORTA, 5)
#define clr_EN_IN0_TO_CAM0 clear_io(PORTA, 5)
#define tgl_EN_IN0_TO_CAM0 toggle_io(PORTA, 5)
#define read_EN_IN0_TO_CAM0 read_io(PORTA, 5)

/* EN_IN0_TO_CAM1 */
#define set_EN_IN0_TO_CAM1 set_io(PORTA, 6)
#define clr_EN_IN0_TO_CAM1 clear_io(PORTA, 6)
#define tgl_EN_IN0_TO_CAM1 toggle_io(PORTA, 6)
#define read_EN_IN0_TO_CAM1 read_io(PORTA, 6)

/* EN_CLOCK_IN */
#define set_EN_CLOCK_IN clear_io(PORTD, 2)
#define clr_EN_CLOCK_IN set_io(PORTD, 2)
#define tgl_EN_CLOCK_IN toggle_io(PORTD, 2)
#define read_EN_CLOCK_IN read_io(PORTD, 2)

/* EN_CLOCK_OUT */
#define set_EN_CLOCK_OUT clear_io(PORTB, 2)
#define clr_EN_CLOCK_OUT set_io(PORTB, 2)
#define tgl_EN_CLOCK_OUT toggle_io(PORTB, 2)
#define read_EN_CLOCK_OUT read_io(PORTB, 2)


/************************************************************************/
/* Registers' structure                                                 */
/************************************************************************/
typedef struct
{
	uint8_t REG_CAM0_EVENT;
	uint8_t REG_CAM1_EVENT;
	uint8_t REG_CAM0_EVENT_CONFIG;
	uint8_t REG_CAM1_EVENT_CONFIG;
	uint8_t REG_START_AND_STOP;
	uint8_t REG_START_AND_STOP_TIMESTAMPED;
	uint32_t REG_START_TIMESTAMP;
	uint32_t REG_STOP_TIMESTAMP;
	uint8_t REG_RESERVED0;
	uint8_t REG_RESERVED1;
	uint8_t REG_CAM0_TRIGGER_CONFIG;
	uint8_t REG_CAM0_TRIGGER_INVERTED;
	uint8_t REG_CAM0_STROBE_SOURCE;
	uint16_t REG_CAM0_TRIGGER_FREQUENCY;
	uint16_t REG_CAM0_TRIGGER_DURATION_US;
	uint8_t REG_RESERVED2;
	uint8_t REG_RESERVED3;
	uint8_t REG_CAM1_TRIGGER_CONFIG;
	uint8_t REG_CAM1_TRIGGER_INVERTED;
	uint8_t REG_CAM1_STROBE_SOURCE;
	uint16_t REG_CAM1_TRIGGER_FREQUENCY;
	uint16_t REG_CAM1_TRIGGER_DURATION_US;
	uint8_t REG_RESERVED4;
	uint8_t REG_RESERVED5;
	uint8_t REG_OUT0_CONFIG;
	uint8_t REG_OUT1_CONFIG;
	uint8_t REG_RESERVED6;
	uint8_t REG_RESERVED7;
	uint8_t REG_OUT_SET;
	uint8_t REG_OUT_CLEAR;
	uint8_t REG_OUT_TOGGLE;
	uint8_t REG_OUT_WRITE;
	uint8_t REG_IN_STATE;
} AppRegs;
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

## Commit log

2021-11-05 First commit.
    [harp camera controller v.1.0 BOM.xlsx, harp camera controller v.1.0.brd, harp camera controller v.1.0.sch]
2021-11-29 First firmware commit.
    [registers.xls]
2021-11-29 Updated PCB to version 1.1.
    [harp camera controller v.1.0 BOM.xlsx, harp camera controller v.1.0.brd, harp camera controller v.1.0.sch]
2022-03-25 Removed 80Hz default frequency.
    [registers.xls]
2022-03-25 Added single frame command.
2022-03-25 Corrected enable of buffers U2, U3, and U4.
    [harp camera controller BOM.xlsx, harp camera controller v.1.1 BOM.xlsx, harp camera controller.brd, harp camera controller.sch]
2022-03-25 Minor corrections.
    [registers.xls]
2022-03-26 Added rear and front panels.
    [copper_bottom.gbr, copper_top.gbr, gerber_job.gbrjob, harp camera controller front panel.brd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]
2022-03-26 Added PCB gerbers.
    [copper_bottom.gbr, copper_top.gbr, gerber_job.gbrjob, profile.gbr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]
2022-04-05 Updated read panel with a square hole for the 12V plug.
    [copper_bottom.gbr, copper_top.gbr, gerber_job.gbrjob, harp camera controller rear panel.brd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]
2022-04-10 Corrected PN of R12
    [harp camera controller BOM.xlsx]
2022-04-13 Updated PCB to version 1.2
    [harp camera controller.brd, harp camera controller.sch]
2022-04-13 Added gerbers for PCB version 1.2
    [copper_bottom.gbr, copper_top.gbr, gerber_job.gbrjob, silkscreen_top.gbr]
2022-04-13 Added camera controller breakout.
    [harp camera controller breakout v1.0 BOM.xlsx, harp camera controller breakout v1.0.brd, harp camera controller breakout v1.0.sch]
2022-05-02 Remapped CLKIN.
    [registers.xls]
2022-05-08 Updated hardware version to match current PCB version.
2022-05-13 Changed 5V output to 5.3V and released PCB v1.2
    [harp camera controller BOM.xlsx, harp camera controller front panel.brd, harp camera controller.brd, harp camera controller.sch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]
2022-05-16 Added text to rear panel.
    [harp camera controller rear panel.brd, silkscreen_top.gbr]
2022-07-08 Added new register START_AND_STOP_TIMESTAMPED.
    [registers.xls]
